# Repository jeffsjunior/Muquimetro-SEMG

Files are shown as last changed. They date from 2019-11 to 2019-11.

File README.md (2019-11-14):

# Muquimetro-SEMG 

## Eletromiografia de Superfície

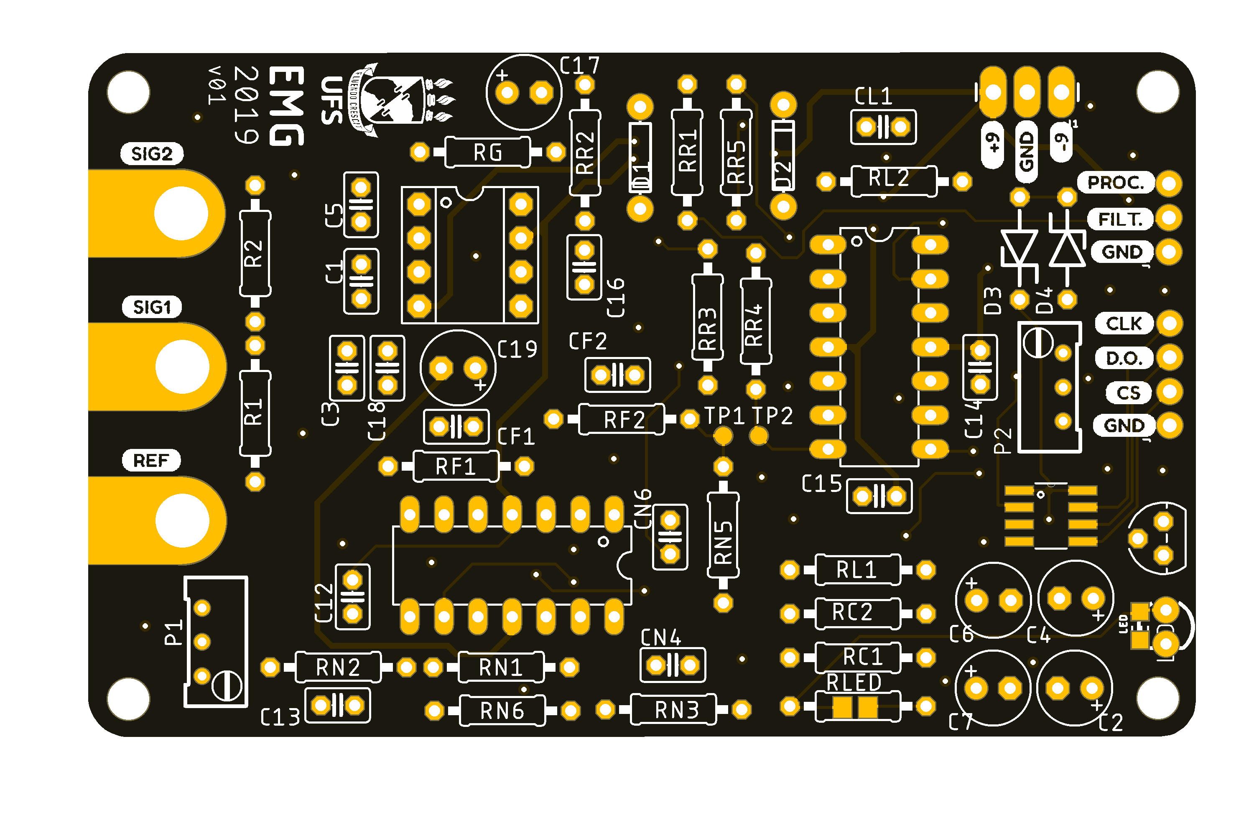
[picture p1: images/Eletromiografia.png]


## Sobre o Projeto

  O Muquímetro é um dispositivo eletrônico que mede a ativação muscular a partir do potencial de ação gerado pelos neurônios motores. A medição ocorre na superfície da pele, por isso o nome Eletromiografia de Superfície (SEMG). A eletromiografia de superfície vem sendo bastante utilizada em diversas áreas, por exemplo, medicina, fisioterapia, robótica, terapia ocupacional. O Muquímetro foi desenvolvido por alunos e professores da Universidade Federal de Sergipe durante a disciplina Eletrônica Aplicada, ofertada pelo curso Engenharia Eletrônica do Departamento de Engenharia Elétrica.

### Aplicações
* Robótica
* Jogos
* Estudo da atividade muscular
* Testes de força, exaustão e fadiga muscular
* Fisioterapia esportiva

## Licença
Todo o material e o Muquímetro estão licenciados de acordo com TAPR Open Hardware License (OHL). O documento contendo informações a respeito da licença encontra-se no arquivo “LICENSE.pdf”.

## Contato

Jefferson Silveira - descomplexando@gmail.com

Link do Projeto: [https://github.com/jeffsjunior/Muquimetro-SEMG](https://github.com/jeffsjunior/Muquimetro-SEMG)

## Participantes do Projeto
* André de Andrade
* Carlos Silva
* Hugo Fontes
* Lean de Oliveira
* Lucas Castro
* Micaelle de Souza
* Raphael Cardoso
* Raul de Andrade
* Renan Sandes
* Renato Fagundes
* Ruan dos Santos
* Shyenne Souza

# Desenvolvido na 

<p align="center">
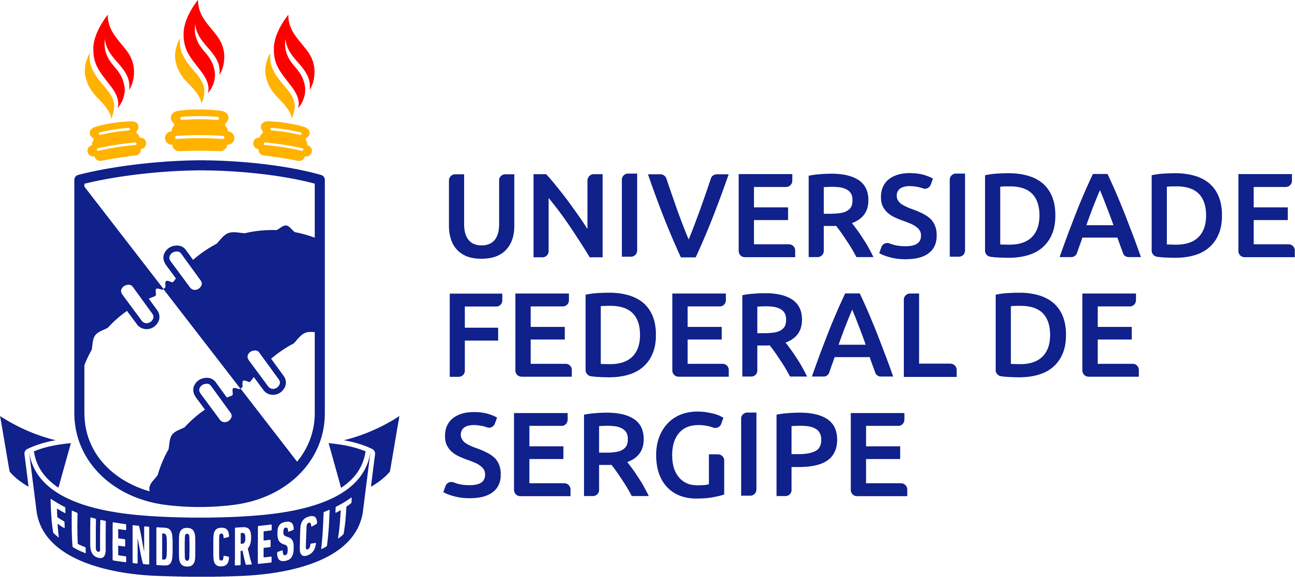
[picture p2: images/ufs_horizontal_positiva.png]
  
</p>

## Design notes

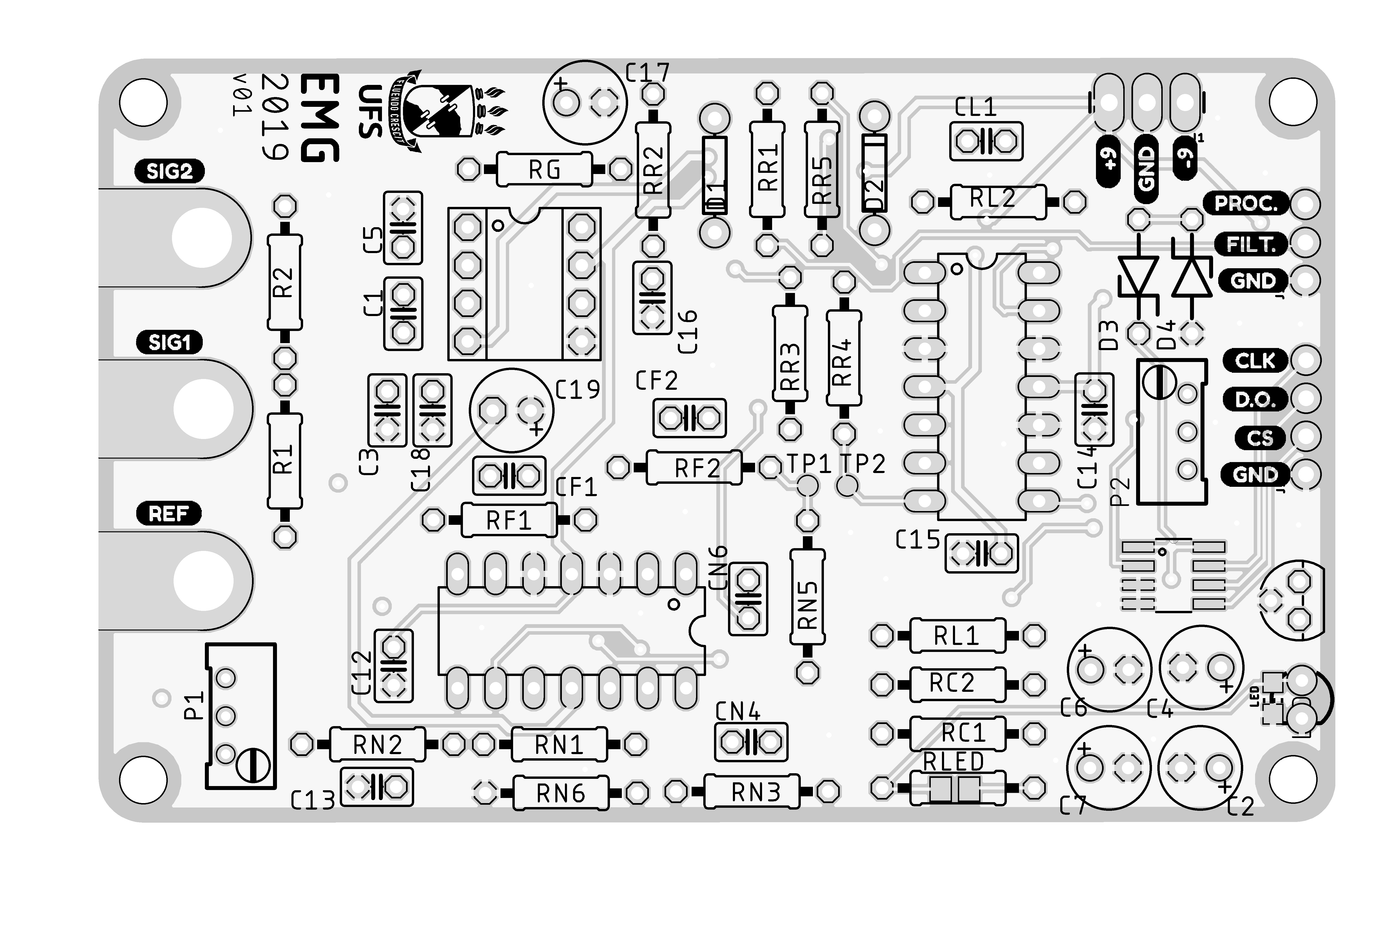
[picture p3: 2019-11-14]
images/Eletromiografia_BW.png

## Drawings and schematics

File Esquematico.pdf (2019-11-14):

G = 112 | G = 100, f1 = 20 Hz, f2 = 500 Hz

## Notch - f0 = 60 Hz

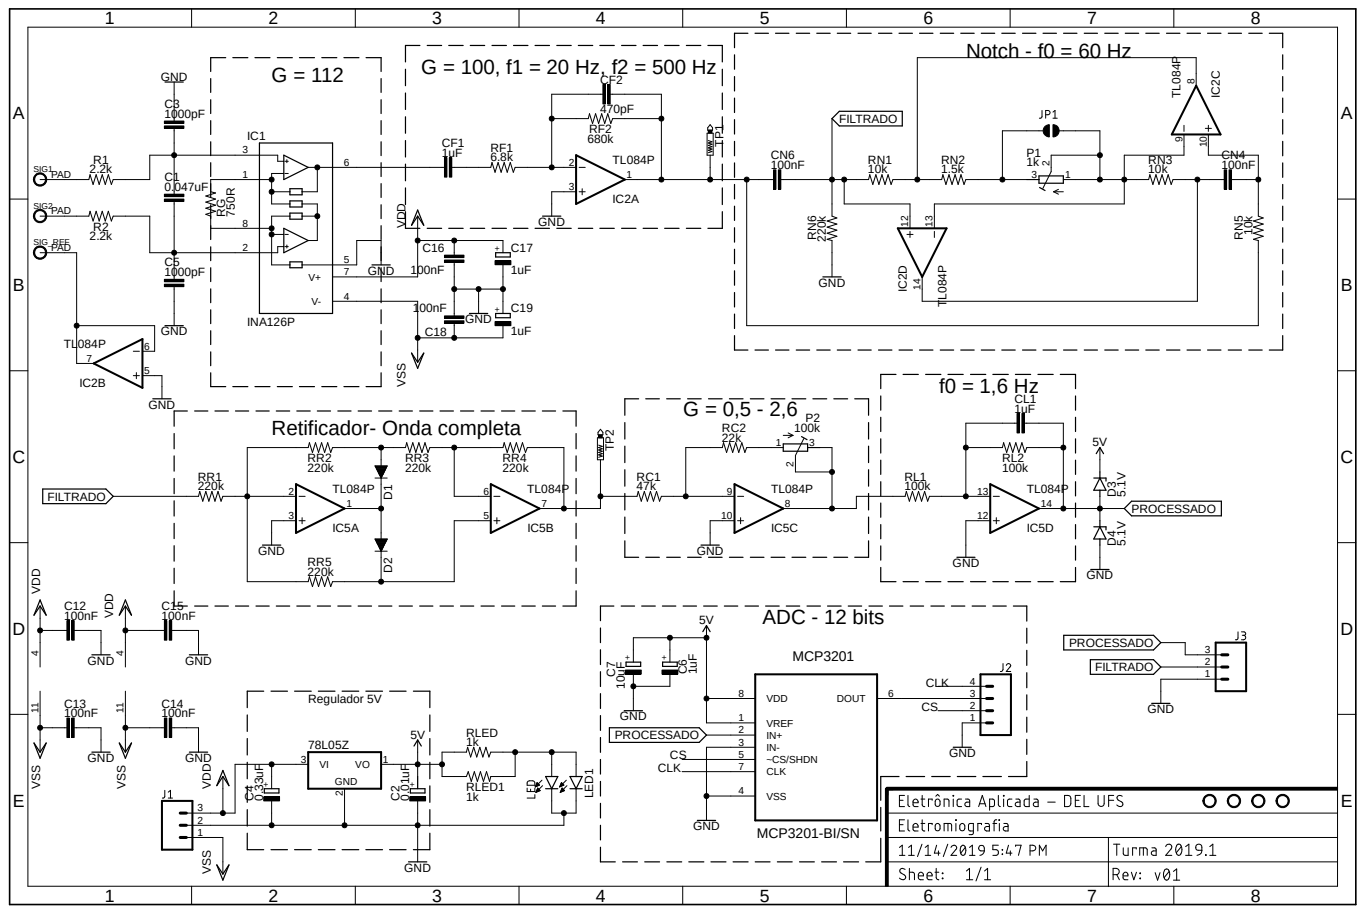
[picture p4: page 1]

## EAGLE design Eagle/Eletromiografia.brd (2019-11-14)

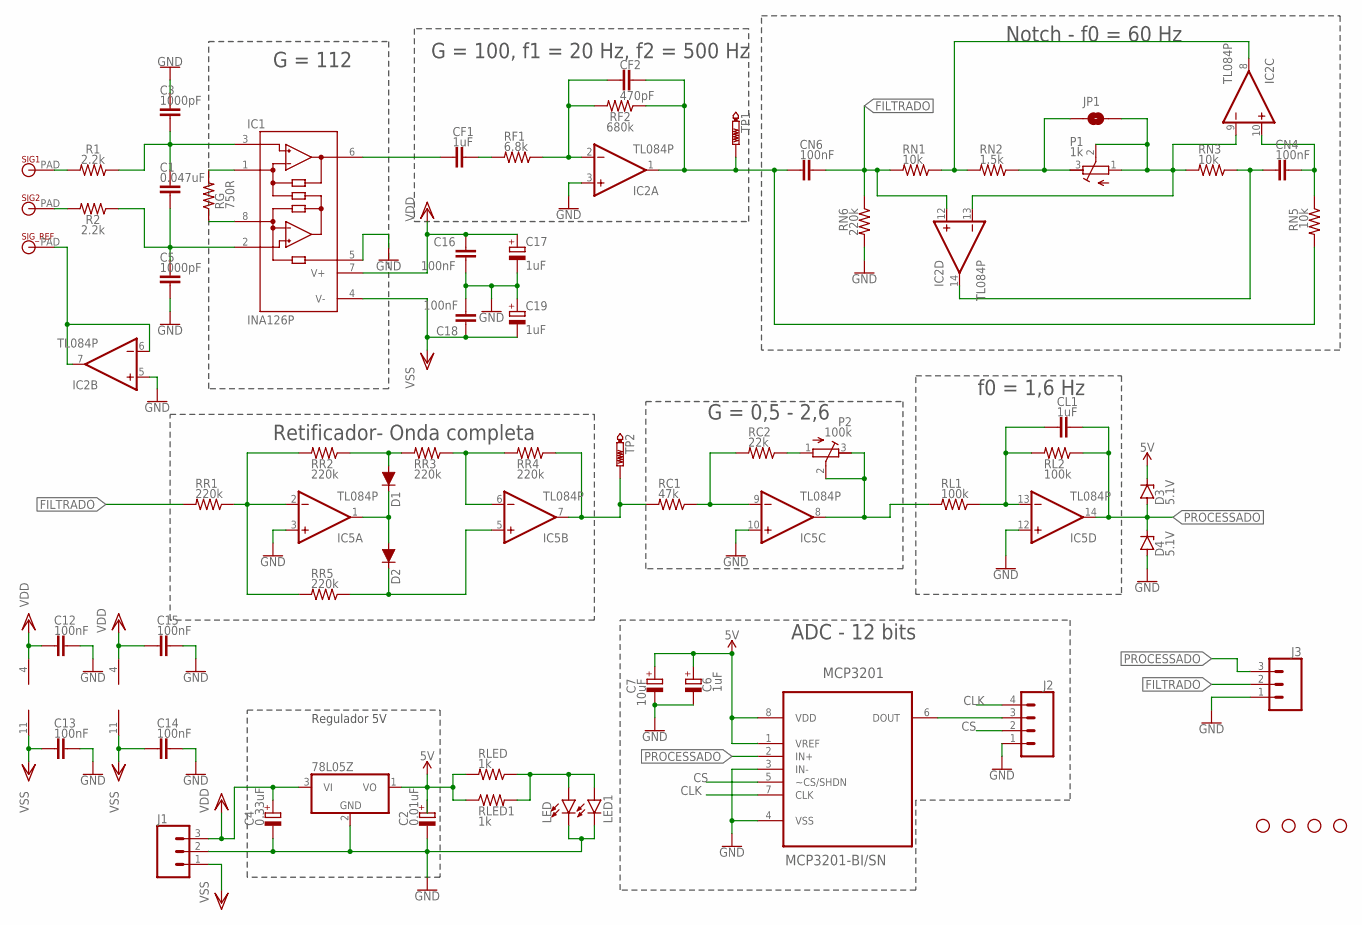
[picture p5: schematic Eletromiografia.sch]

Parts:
C1: 0.047uF; C025-025X050
C2: 0.01uF; E2,5-6
C3, C5: 1000pF; C025-025X050
C4: 0.33uF; E2,5-6
C6, C17, C19: 1uF; E2,5-6
C7: 10uF; E2,5-6
C12, C13, C14, C15, C16, C18: 100nF; C025-025X050
CF1: 1uF; C025-025X050
CF2: 470pF; C025-025X050
CL1: 1uF; C025-025X050
CN4, CN6: 100nF; C025-025X050
D1, D2: 200mA/100V/1V; DIODE-1N4148
D3, D4: 5.1V; ZDIO-7.5
H1, H2, H3, H4: STAND-OFFTIGHT; STAND-OFF-TIGHT
IC1: INA126P; DIL08
IC2, IC5: TL084P; DIL14
IC3: 78L05Z; TO92
J1: CONN_03LONGPADS; 1X03_LONGPADS
J2: CONN_041X04_NO_SILK; 1X04_NO_SILK
J3: CONN_031X03_NO_SILK; 1X03_NO_SILK
JP1: JUMPER-SMT_2_NO_NO-SILK_ROUND; SMT-JUMPER_2_NO_NO-SILK_ROUND
LED: LED3MM; LED_3MM
LED1: LEDCHIP-LED0805; CHIP-LED0805
MCP3201: MCP3201-BI/SN; SOIC127P600X175-8N
P1: 1k; RTRIM64W
P2: 100k; RTRIM64W
R1, R2: 2.2k; 0207/10
RC1: 47k; 0207/10
RC2: 22k; 0207/10
RF1: 6.8k; 0207/10
RF2: 680k; 0207/10
RG: 750R; 0207/10
RL1, RL2: 100k; 0207/10
RLED: 1k; 0207/10
RLED1: 1k; R0805
RN1, RN3, RN5: 10k; 0207/10
RN2: 1.5k; 0207/10
RN6: 220k; 0207/10
RR1, RR2, RR3, RR4, RR5: 220k; 0207/10
SIG1, SIG2: MICROBIT_PAD
SIG_REF: MICROBIT_PAD
TP1, TP2: PTR1B1,27; B1,27

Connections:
5V: C2.+, C6.+, C7.+, D3.C, IC3.1 (VO), MCP3201.1 (VREF), MCP3201.8 (VDD), RLED.2, RLED1.1
CLK: J2.4, MCP3201.7 (CLK)
CS: J2.2, MCP3201.5 (~CS/SHDN)
FILTRADO: CN6.2, IC2.12 (+IN), J3.2, RN1.2, RN6.1, RR1.2
GND: C2.-, C3.2, C4.-, C5.1, C6.-, C7.-, C12.2, C13.2, C14.2, C15.2, C16.1, C17.-, C18.2, C19.+, D4.A, IC1.5 (REF), IC2.3 (+IN), IC2.5 (+IN), IC3.2 (GND), IC5.3 (+IN), IC5.10 (+IN), IC5.12 (+IN), J1.2, J2.1, J3.1, LED.K (C), LED1.C, MCP3201.3 (IN-), MCP3201.4 (VSS), RN6.2
unnamed: IC1.1 (RG), RG.2
unnamed: IC1.8 (RG), RG.1
unnamed: C1.2, C3.1, IC1.3 (+IN), R1.1
unnamed: R1.2, SIG1.PAD
unnamed: IC2.6 (-IN), IC2.7 (OUT), SIG_REF.PAD
unnamed: CF1.1, IC1.6 (OUT)
unnamed: CF1.2, RF1.2
unnamed: CF2.1, IC2.2 (-IN), RF1.1, RF2.2
unnamed: JP1.1, P1.3 (E), RN2.1
unnamed: CF2.2, CN6.1, IC2.1 (OUT), RF2.1, RN5.2, TP1.TP
unnamed: CN4.2, IC2.10 (+IN), RN5.1
unnamed: CN4.1, IC2.14 (OUT), RN3.1
unnamed: C1.1, C5.2, IC1.2 (-IN), R2.1
unnamed: R2.2, SIG2.PAD
unnamed: IC2.8 (OUT), RN1.1, RN2.2
unnamed: IC2.9 (-IN), IC2.13 (-IN), JP1.2, P1.1 (A), P1.2 (S), RN3.2
unnamed: J2.3, MCP3201.6 (DOUT)
unnamed: IC5.2 (-IN), RR1.1, RR2.2, RR5.2
unnamed: D1.A, RR2.1, RR3.2
unnamed: D1.C, D2.A, IC5.1 (OUT)
unnamed: D2.C, IC5.5 (+IN), RR5.1
unnamed: IC5.6 (-IN), RR3.1, RR4.2
unnamed: IC5.7 (OUT), RC1.2, RR4.1, TP2.TP
unnamed: IC5.9 (-IN), RC1.1, RC2.2
unnamed: P2.1 (A), RC2.1
unnamed: IC5.8 (OUT), P2.2 (S), P2.3 (E), RL1.2
unnamed: CL1.1, IC5.13 (-IN), RL1.1, RL2.2
unnamed: LED.A, LED1.A, RLED.1, RLED1.2
PROCESSADO: CL1.2, D3.A, D4.C, IC5.14 (OUT), J3.3, MCP3201.2 (IN+), RL2.1
VDD: C4.+, C12.1, C15.1, C16.2, C17.+, IC1.7 (V+), IC2.4 (V+), IC3.3 (VI), IC5.4 (V+), J1.3
VSS: C13.1, C14.1, C18.1, C19.-, IC1.4 (V-), IC2.11 (V-), IC5.11 (V-), J1.1

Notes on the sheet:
G = 112
G = 100, f1 = 20 Hz, f2 = 500 Hz
Notch - f0 = 60 Hz
Retificador- Onda completa
G = 0,5 - 2,6
f0 = 1,6 Hz
ADC - 12 bits
Regulador 5V

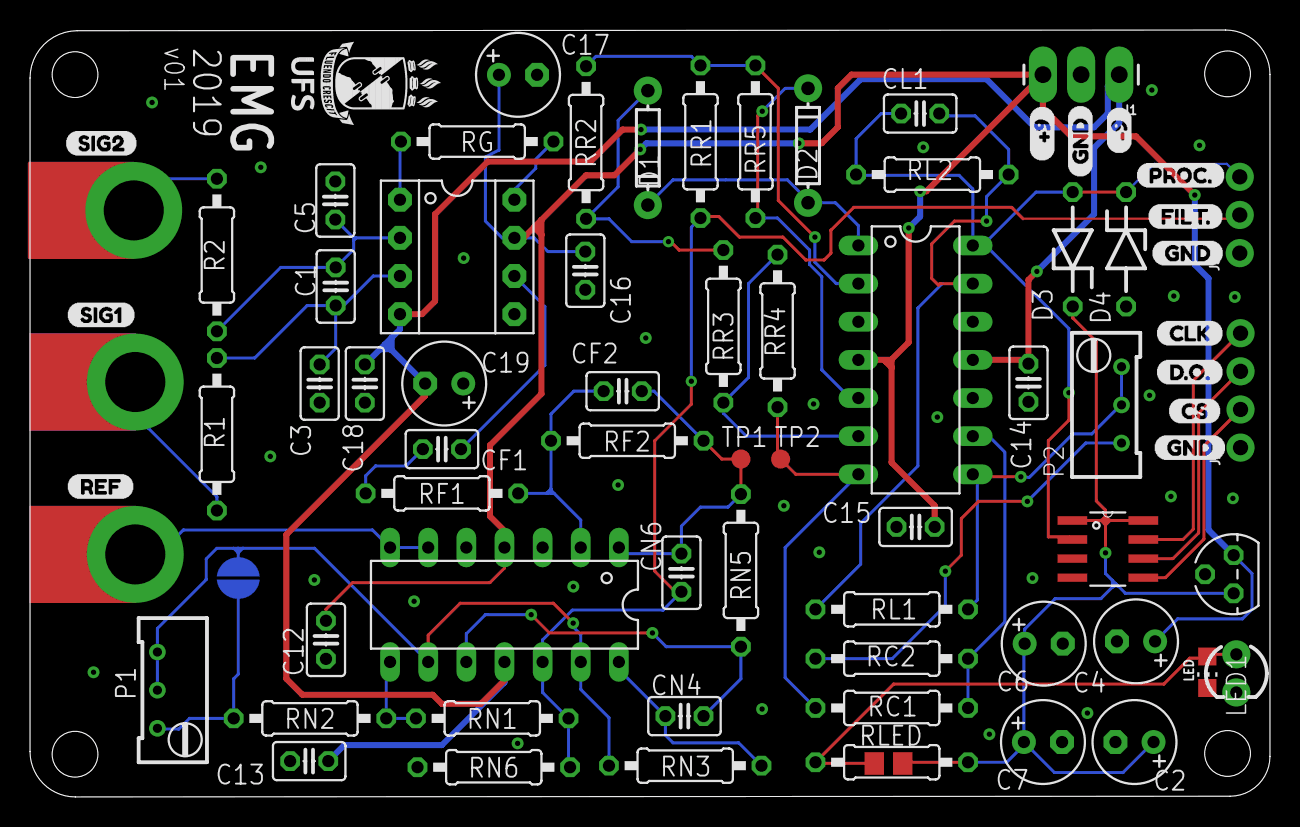
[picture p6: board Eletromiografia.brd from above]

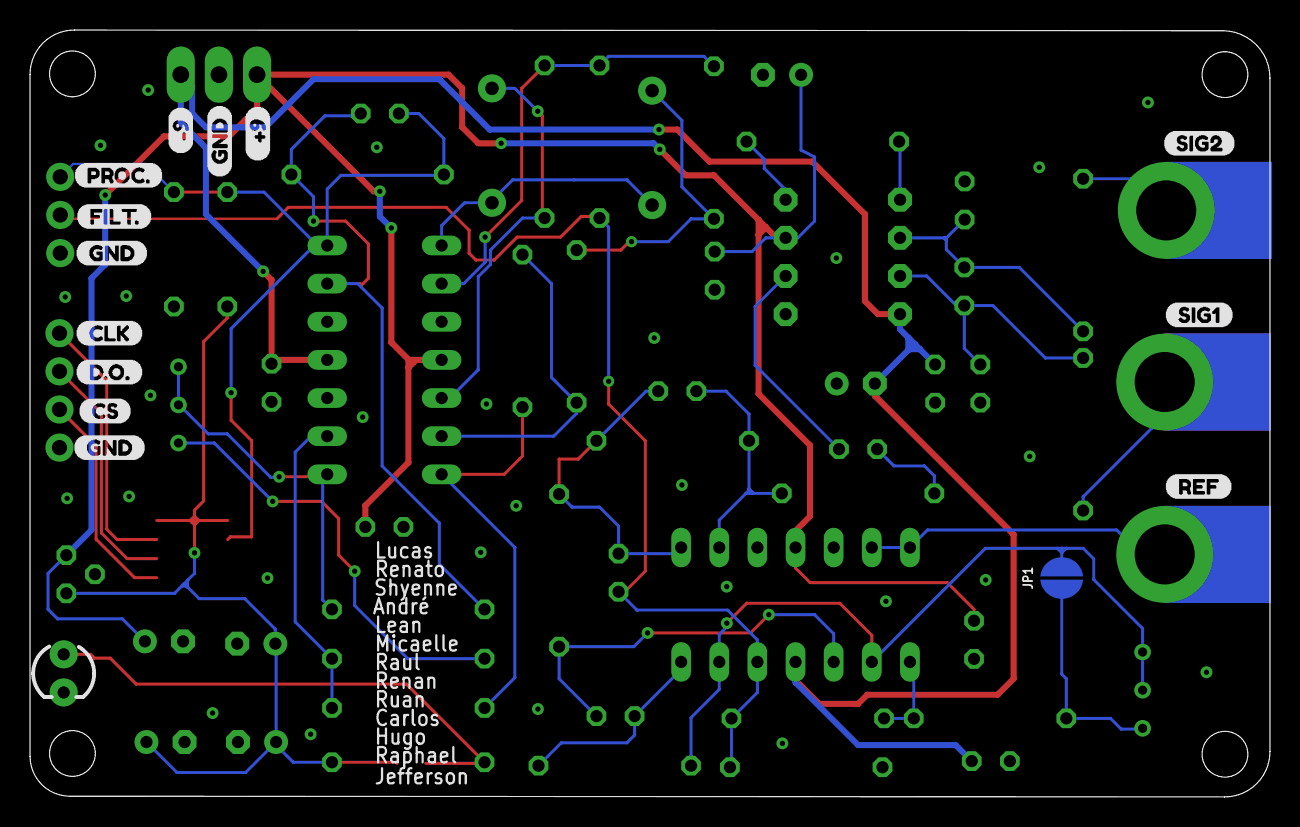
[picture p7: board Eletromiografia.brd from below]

Board: 2 copper layers, 82.6 x 51.1 mm, 93 parts (14 on the bottom side), 36 nets.

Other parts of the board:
U$2, U$18: _#98
U$3, U$20: #99
U$4, U$7, U$11, U$19, U$23, U$27: GND7
U$5, U$21: PROC#3
U$6, U$22: FILT#4
U$8, U$24: CLK6
U$9, U$25: D#O#10
U$10, U$26: CS5
U$12, U$15: SIG21
U$13, U$16: SIG12
U$14, U$17: REF0

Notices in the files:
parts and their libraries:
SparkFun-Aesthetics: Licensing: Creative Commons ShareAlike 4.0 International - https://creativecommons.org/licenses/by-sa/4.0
